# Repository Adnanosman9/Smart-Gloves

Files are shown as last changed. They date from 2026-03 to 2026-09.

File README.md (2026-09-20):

<h1 align="center">
  BdSL Translator Glove
  <br>
</h1>

<h4 align="center">
A wearable glove that translates Bangladeshi Sign Language (BdSL) into speech in real-time
</h4>

<div align="center">





</div>

## What is this?

A lot of deaf people in Bangladesh have no easy way to talk to people who don't know sign language. I wanted to fix that. Not with a camera setup that needs good lighting and a phone pointed at you the whole time, but something you actually wear and carry around. So I built it into a glove.

## How it works

There are two ways to build this depending on what you have access to.

**Option 1: Commercial flex sensors (what I recommend)**
Five 2.2" flex sensors go along each finger, held down by TPU guide segments I designed and printed. When you bend a finger, the sensor's resistance changes and the ADC picks that up. Simple and reliable.

**Option 2: Conductive TPU (only if you have your own printer)**
I originally wanted to skip commercial sensors entirely and just print the finger segments in Conductive TPU. It's piezoresistive, so resistance shifts as it bends, same idea. But no commercial print service carries conductive TPU filament, so unless you have your own printer and the filament already, this option is off the table. I learned that the hard way.

Either way, a **XIAO ESP32-C3** reads all the sensor values alongside orientation data from an **MPU-6050** IMU, maps them into a hand-geometry profile, and classifies the sign. Everything gets sent over Bluetooth LE.

No cameras. Works in the dark. Works outside. Works anywhere.

Print the finger guides here: [for flex sensors](https://github.com/Adnanosman9/Smart-Gloves/tree/main/CAD%20for%20flex%20sensor) | [for 3D-printed sensor](https://github.com/Adnanosman9/Smart-Gloves/tree/main/CAD_3d%20printed%20sensor)

---

## Addressing the Hack Club Review

The first version got flagged for two things:

> *"$80 seems a bit much for flex sensors"* and *"your CAD only shows a box, could you maybe design some flexible structure out of TPU?"*

Both fair. Here's what I changed.

**On the cost:** The original $80 estimate was for 4" flex sensors. I've since switched to 2.2" sensors at $6.86 each, which brings the total down to $68.60. BdSL uses both hands, so that's 10 fingers, 10 sensors, and $68.60 is already the cheapest I could get this to work. Not padding anything, that's just what flex sensors cost.

**On the CAD:** I redesigned the finger part properly. Each finger now has a TPU guide segment that holds the flex sensor flat against the joint. The glove actually looks like a glove now, not just a box with wires coming out of it. The wrist hub is still a box (it has to be, there's a PCB in there), but the hand part is done.

---

## The Finger Guide System

Credit to [zackfreedman](https://www.thingiverse.com/thing:1606915) for the original parametric ring glove design that I built on top of.

Find the STL [here](https://github.com/Adnanosman9/Smart-Gloves/blob/main/CAD%20for%20flex%20sensor/Ring_Glove_Parametric.stl).

Each finger gets a TPU channel segment. The sensor slides in and stays put mechanically, no glue, no tape. I made two sizes: "Long" for the index, middle, and ring fingers, and "Short" for the thumb and pinky since those are shorter and sit at a different angle.

White TPU, printable by any FDM service that does flexible filament.

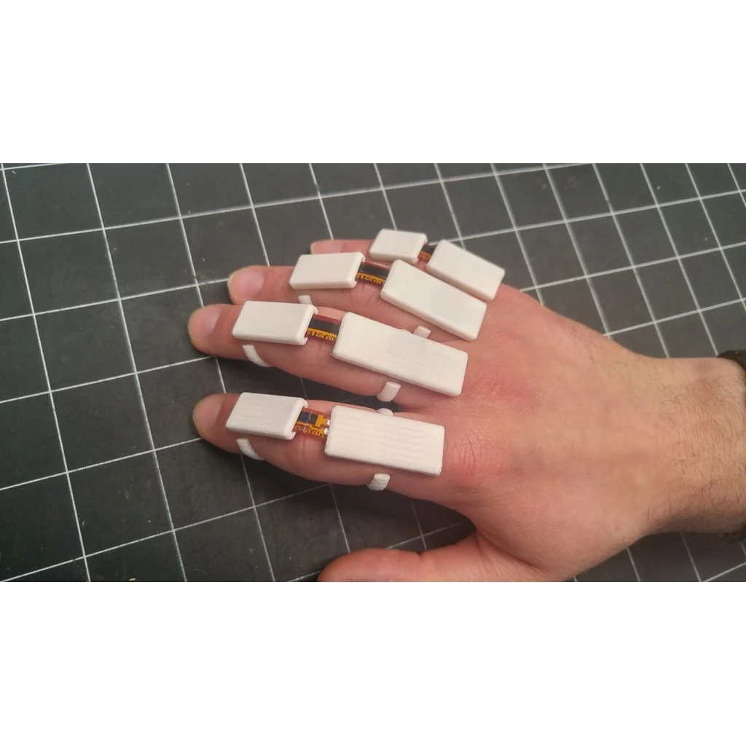
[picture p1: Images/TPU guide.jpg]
TPU finger guide segments


---

## The PCB

I designed a low-profile wrist hub in KiCad to keep everything in one place. A few things worth noting:

The **XIAO ESP32-C3** was the obvious pick: tiny footprint, built-in BLE, enough ADC pins for all five sensors. I used a **47kΩ voltage divider** on each sensor input because the flex sensors are high-impedance and need it to read reliably. Threw in **0.1µF decoupling caps** on the sensor lines too after I noticed noise in early simulations.

DRC came back 0 errors. There are some silkscreen warnings but those are just text placement things, nothing that affects the board.

**Schematic:**

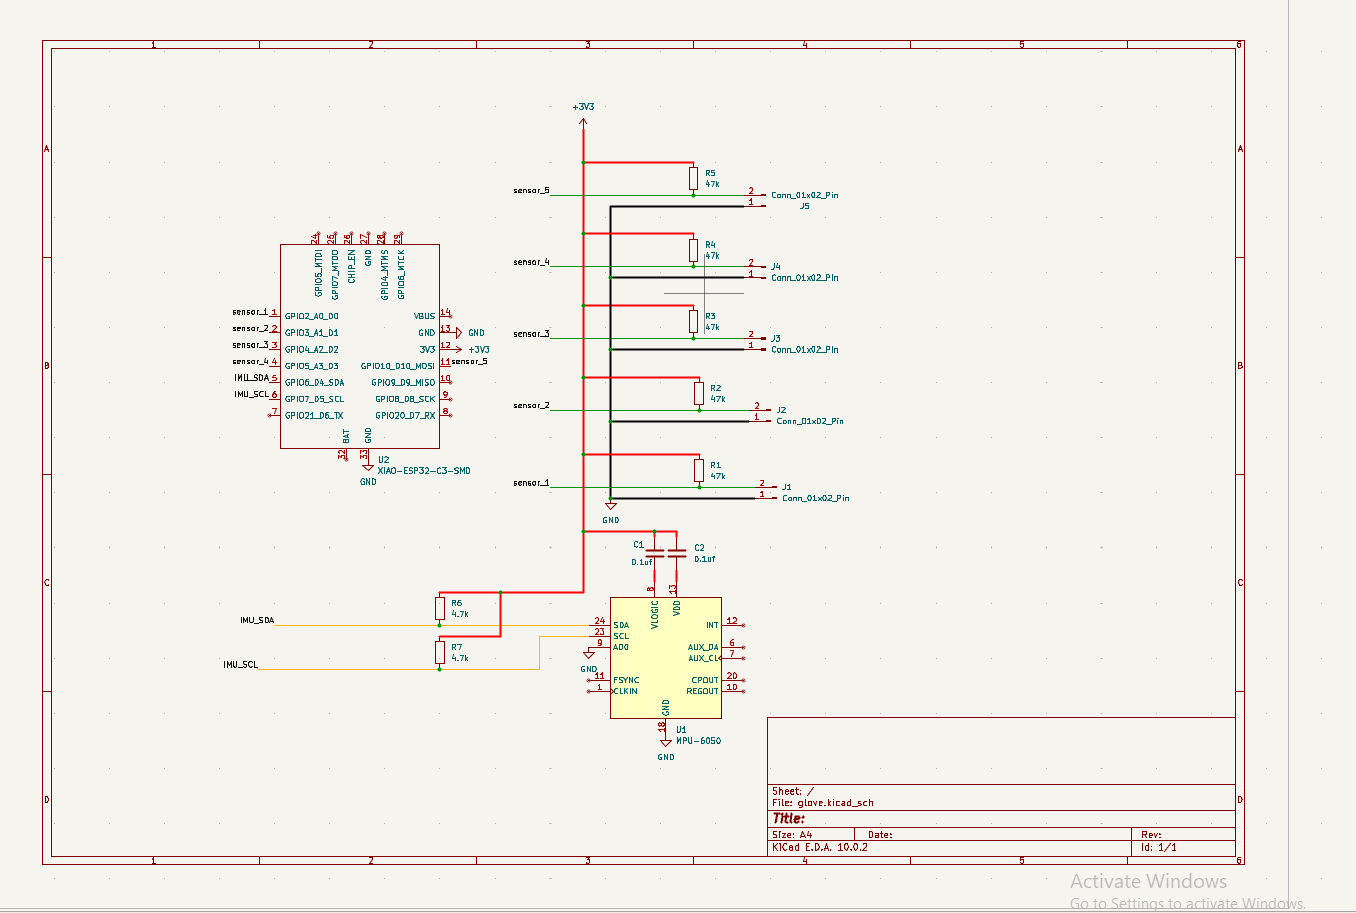
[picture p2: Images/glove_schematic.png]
Schematic


**PCB Layout:**

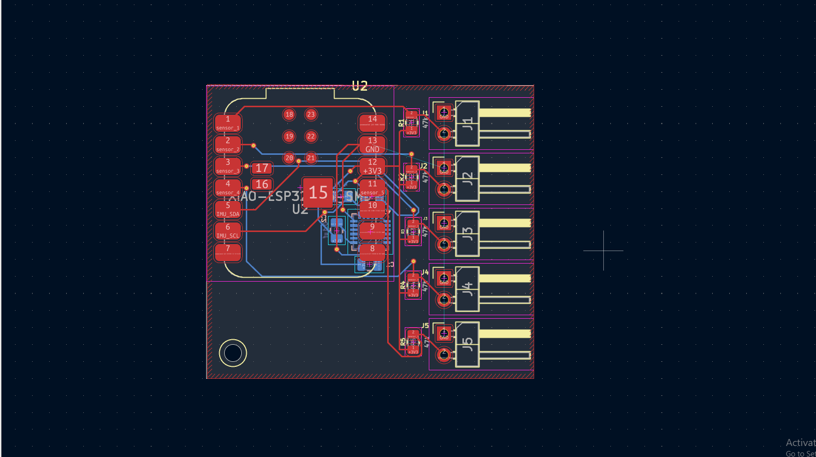
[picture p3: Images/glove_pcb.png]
PCB Layout


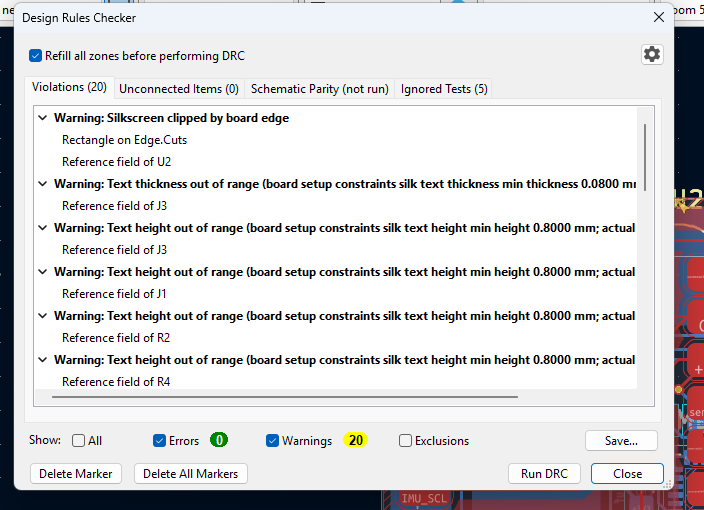
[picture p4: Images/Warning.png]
KiCad DRC: 0 errors, silkscreen warnings only


---

## The Enclosure

Designed in Fusion 360. Sits on the wrist, low-profile. The whole electronics module attaches with Velcro so you can pull it off and actually wash the glove fabric.

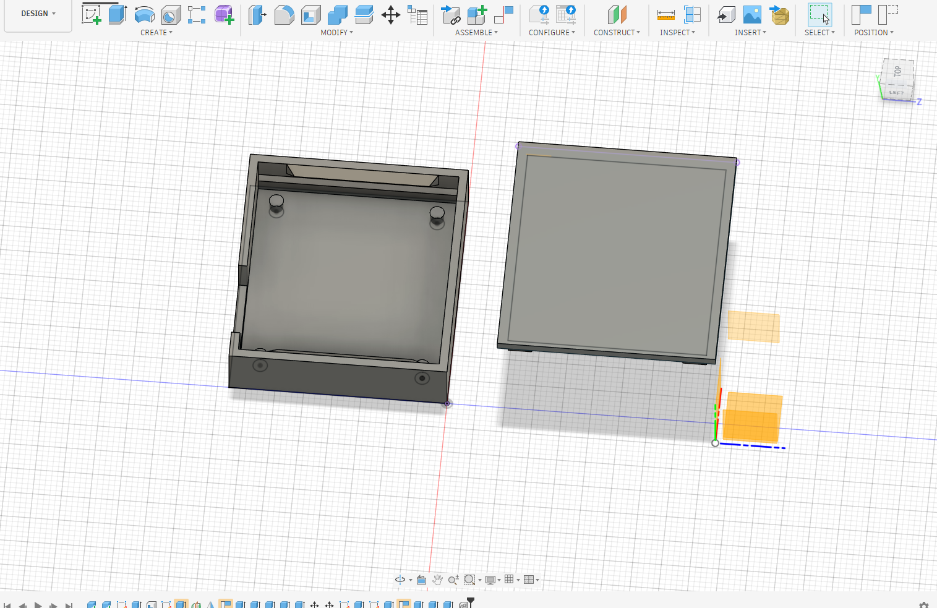
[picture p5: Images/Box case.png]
Wrist hub box


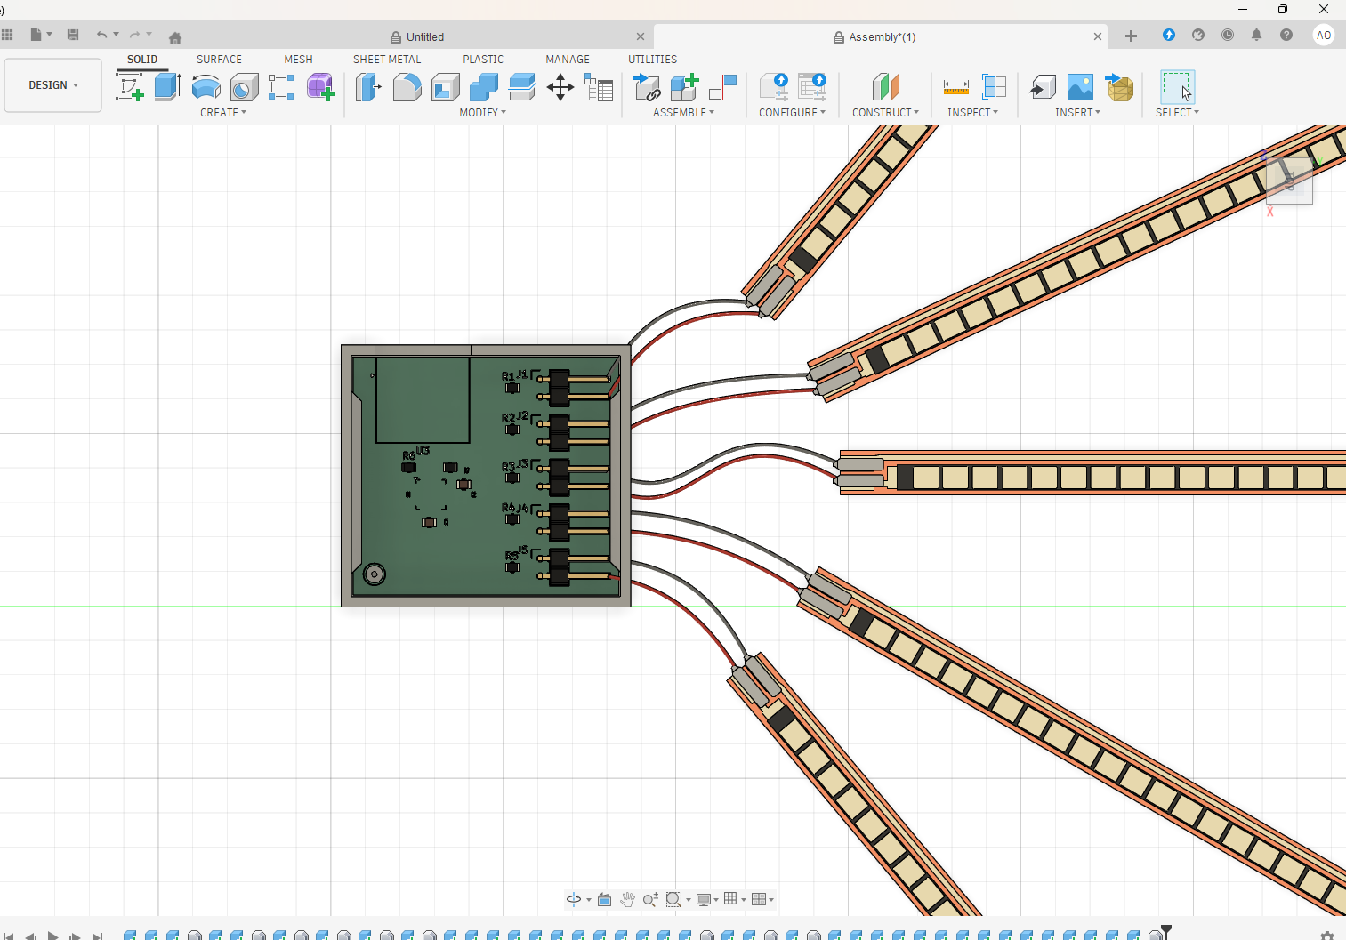
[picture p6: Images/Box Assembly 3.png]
Assembly render


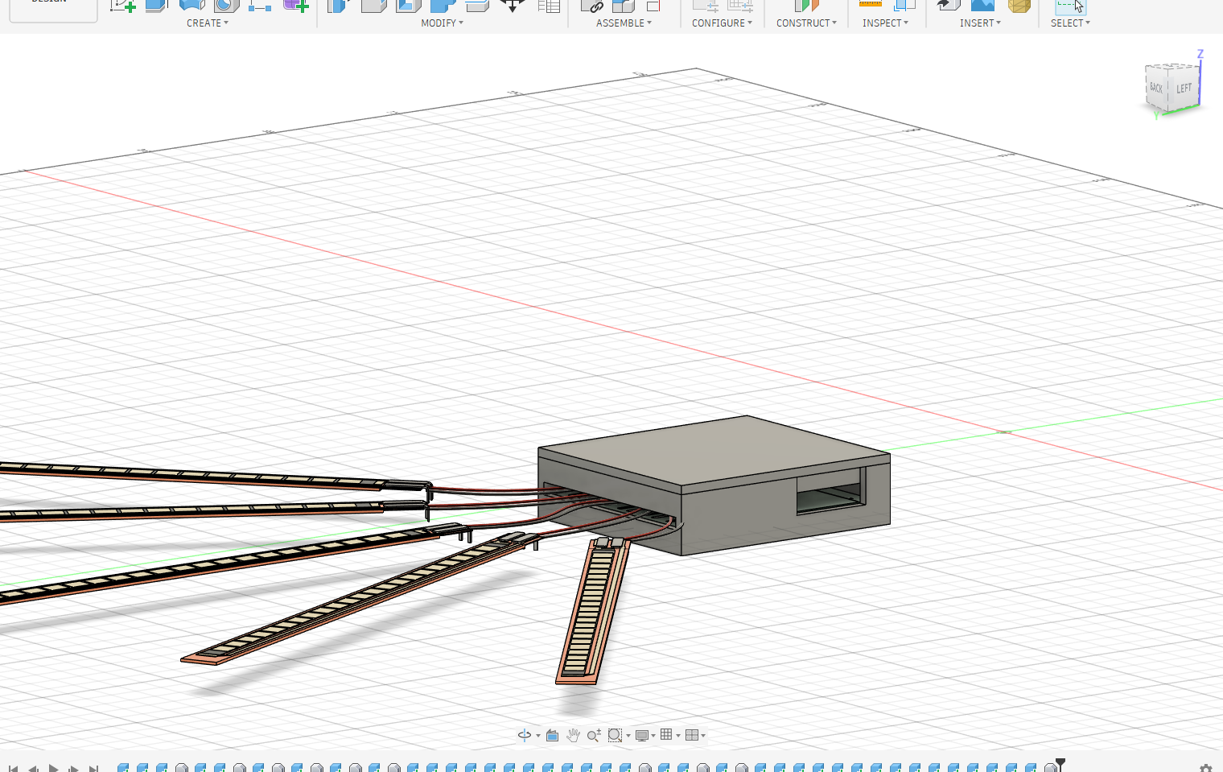
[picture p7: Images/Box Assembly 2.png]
Assembly render 2


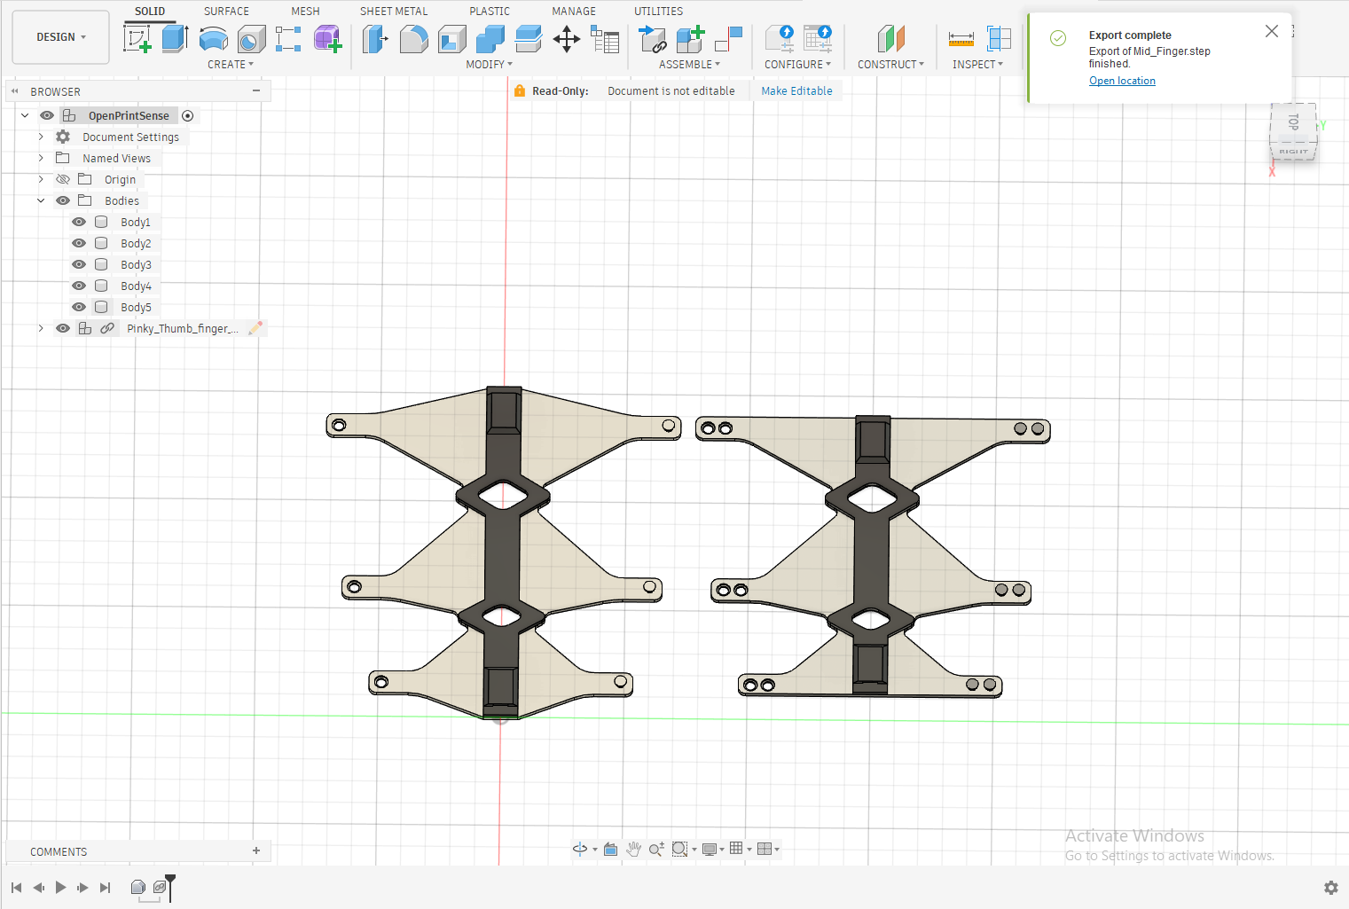
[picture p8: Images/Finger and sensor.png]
Finger segment with sensor


---

## ⚠️ Heads up on the firmware

I haven't physically tested the firmware yet. There's a real chance there are I2C pin mismatches, wrong GPIO assignments, or sensor init issues that won't show up until you actually flash and boot it. Please double-check every pin assignment against the schematic before you flash anything. First boot will probably need some debugging.

## Bill of Materials

[BOM is here](bom/BOM.csv)

## Credits

- [KiCad](https://www.kicad.org/) for PCB design
- [Autodesk Fusion 360](https://www.autodesk.com/products/fusion-360/) for the enclosure
- [Open Print Sense](https://github.com/PaBu04/OpenPrintSense/tree/main) for the 3D-printed sensor approach
- [zackfreedman](https://www.thingiverse.com/thing:1606915) for the parametric finger guide base
- [Hack Club](https://hackclub.com/) for the support

---

> GitHub [@Adnanosman](https://github.com/Adnanosman9)

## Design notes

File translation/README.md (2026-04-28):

# Translation Firmware

This is the main firmware for both gloves.  
Use this after calibration is done and your ML model is ready.

---

## Libraries

Install from Arduino Library Manager:

- ESP32 BLE Arduino (usually comes with ESP32 board package)
- Adafruit MPU6050
- Adafruit Unified Sensor
- ArduinoJson

---

## Step 1 - Calibration (Do this properly)

You need to calibrate **each glove separately**.  
Flex sensor readings are never exactly the same between hands.

Flash `calibration.ino`, open Serial Monitor, then:

1. Keep all fingers fully open (~5 seconds)
2. Then close all fingers fully (~5 seconds)
3. Copy the `openVals` and `closedVals` printed in Serial

Paste them into both:
- `glove_left.ino`
- `glove_right.ino`

```cpp
const int openVals[5]   = {your values};
const int closedVals[5] = {your values};
```

## Step 2 - Flash to Gloves

| File              | Glove | BLE Name  |
| ----------------- | ----- | --------- |
| `glove_left.ino`  | Left  | `SIGNO-L` |
| `glove_right.ino` | Right | `SIGNO-R` |

## Step 3 - Connect to App

Open the SIGNO app and press Connect.

It should automatically detect:
- SIGNO-L
- SIGNO-R

<br>

## *__I didn't have any physical component and don't have yet, so now I can't give bebug solution for every problem that will show up, I will add it up soon.__*

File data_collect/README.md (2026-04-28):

# Dataset Collection Firmware

This firmware is used to record gesture data from both gloves over USB serial.  
Each glove saves its own CSV file. Later, both files are merged and used to train the model.

---

## Requirements

- 2 gloves with ESP32-C6  
- 2 USB cables (one for each glove)  
- Arduino IDE or PlatformIO  
- Libraries:
  - Adafruit MPU6050  
  - Adafruit Unified Sensor  

---

## Before You Start (Don’t Skip This)

Open both `.ino` files and update the calibration values:

```cpp
const int openVals[5]   = {...};
const int closedVals[5] = {...};
```
Use the values from your calibration step.

If these are wrong, your flex readings will be inaccurate and you’ll likely have to redo your dataset. It’s worth checking twice here.

Recording Process
## 1. Flash both gloves

Upload:

```data_collect_left.ino``` → left glove

```data_collect_right.ino``` → right glove

## 2. Open Serial Monitors

Open two Serial Monitor windows (one for each glove)

On startup, you should see:

```label,thumb,index,middle,ring,pinky,ax,ay,az,gx,gy,gz,timestamp```

If you don’t see this, check:
- Correct COM port
- Baud rate
- Cable connection

## 3. Recording Gestures

For each gesture:
- Form the gesture and hold it steady
- Type the label (e.g. HELLO) into both Serial Monitors and press Enter
- Keep holding the gesture while it records
- Each glove records ~30 samples, then stops automatically

Repeat for all gestures.

> Try to stay still while recording — even small movements can add noise.

## 4. How Much Data?

- Minimum: ~50 samples per gesture
- Recommended: 80–100 samples

> More variation usually helps the model perform better.

## 5. Save the Data

Copy the Serial Monitor output from each window and save as:
- left_hand.csv
- right_hand.csv

## After Recording

Go to the ml/ folder and run the training script.

It will:
- Merge both CSV files using timestamps
- Train a Random Forest classifier
- Export modelWeights.js for use in the app

## CSV format reference 

| Column        | Description                            |
| ------------- | -------------------------------------- |
| label         | gesture name                           |
| thumb → pinky | flex values (0 = open, 1 = fully bent) |
| ax, ay, az    | accelerometer (g)                      |
| gx, gy, gz    | gyroscope (rad/s)                      |
| timestamp     | time in ms                             |

## Notes / Common Issues
- Both gloves need to record at the same time, otherwise merging won’t work properly
- On Windows, COM ports can change when reconnecting devices
- If Serial Monitor doesn’t connect, recheck the selected port
- If flex readings look off, redo calibration before collecting more data

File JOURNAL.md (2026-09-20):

<!--
  This journal is auto generated by Stasis.
-->

# 5/19/2026 7 PM - Changes due to sourcing issues

_Time spent: 2h_

During making the BOM, I found out that no commercial printing service prints Conductive TPU filament. 

**So it's not possible to print flex sensor out og conductive TPU unless you have own 3d printer and filament**

I re-added commercial flex sensors.

> **Flex sensors are just expensive, there's no way around it. BdSL uses both hands, so that's 10 fingers, 10 sensors. The cheapest viable 2.2" option is ~$5/sensor, which puts the total at $50. That's already the budget option. The $50 isn't extravagant; it's the floor.**





# 5/10/2026 3 PM - Commercial Sensors to Integrated 3D-Printed Hardware

_Time spent: 2h_

In the first phase of SIGNO, our real-time Sign Language translation glove relied on off-the-shelf commercial flex sensors. While functional, these sensors posed three major issues:

- **Cost: At $15–$20 per finger, the glove was too expensive for mass adoption.**

- **Durability: The rigid "box-and-wire" connection points were prone to mechanical failure.**

### **The Pivot: Sensor-less Architecture**

We’ve transitioned to a monolithic, dual-material 3D-printed exoskeleton. Instead of buying sensors, we are printing them directly into the glove's structure.

1. **Using Conductive TPU (Carbon-infused) for the sensing traces and Standard TPU for the structural base. This creates a piezoresistive effect where bending the finger changes the electrical resistance.**

2. **Shifted to the XIAO ESP32-C3. It’s incredibly small, supports Bluetooth LE for mobile app connectivity, and features a built-in battery management system for a truly wireless experience.**

3. **Developed a 4-part modular system (Long segments for long fingers, Short segments for the thumb/pinky) to ensure a universal fit and easier maintenance.**

By moving to integrated 3D-printed sensors, we have reduced the sensor BOM (Bill of Materials) cost by over 50$. This shift moves SIGNO from an "expensive prototype" to a "scalable assistive technology."








# 4/2/2026 10 AM - Revived the unfinished

_Time spent: 0.01666666666666667h_

This was a project on blueprint, but it was not finished, now i imported it to Stasis here. 











# 3/13/2026 12 PM - Finally, the firmware exists

_Time spent: 8h_

## The Brain and Neurons

Okay so the hardware has been sitting there looking pretty for a while now. Today I actually wrote the firmware. All of it.

Added a proper directories for each;
- [Data Collect](https://github.com/Adnanosman9/Smart-Gloves/tree/main/data_collect) - for recording labeled gesture CSVs from both gloves
- [Translation](https://github.com/Adnanosman9/Smart-Gloves/tree/main/translation) - the main BLE firmware that streams sensor data to the app
- [App](https://github.com/Adnanosman9/Smart-Gloves/tree/main/app) - the React Native app that connects, classifies and plays sign gesture loud

Also there is a caution that the firmware isn't physically tested yet because honestly it probably has at least one I2C pin mismatch and I'd rather admit that upfront than pretend everything works.

The SDA/SCL pins in the README said GPIO 6/7 but the schematic says IO8/IO9. Classic. Fixed that too.

At least the glove looks good while the firmware is mid.








# 2/13/2026 12 PM - 404

_Time spent: 1h_

There is a special kind of problem in writing `i2c_read_bytes()` while I have nothing connected to the pins. I'm currently simulating the project gestures with random number of values of flex sensor and IMU.

HOnestly, This things is a total frustration when I can't check what I am writing.





# 2/12/2026 9 PM - Repository Updated

_Time spent: 1h_

After finalizing the hardware designs, spent some time to arrange every step file and PCB gerber file in a folder. Also added several images showing the path. This project has a snap fit box and a PCB holding Microcontrollers and IMU. To make it understandable I tried to make the read me perfect. I guess it will be a good overview to determine why and how the project is made. 

Repo : [GitHub](https://github.com/Adnanosman9/Smart-Gloves)

Github



# 2/12/2026 3 PM - PCB warnings

_Time spent: 1h_

I was just about to export my Gerber files when KiCad decided to humble me with 2 Warnings.
I thought I made any kind of mistake but at the end as usual I found out that I accidently deleted my copper GND layer.

After adding the copper layer, here was 2 warnings and thoose were just for a silkscreen boundery and I think it doesn't create mess. 

_glove — PCB Editor 2_12_2026 3_03_32 PM



# 2/10/2026 11 PM - Made a snap fit box case.

_Time spent: 1h_

To place the pcb on the glove properly, I made a box to place the PCB properly. I used fusion 360 to make that. I made enough holes in the case to connect the external wires and flex sensors.

Box;
Box case

Box with wiring
Box Assembly 2




# 2/10/2026 8 PM - I created a PCB

_Time spent: 1.5h_

Flex sensor is a variable resistor that needs voltage devider to give values. To connect every flex sensor with the microcontroller it will need many cabkle and as we are planning to install it on hands then too much wires might look messy. To avoid these messy problems we are creating a PCB with esp32 c6, MPU6050 on board and 5 2pin connectors to connect Fles sensors externally. 

Glove_PCB

Glove_Schemetic




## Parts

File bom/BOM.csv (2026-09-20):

Name | Purpose | Qty | Total (USD) | Link | Distributor | Note
Flex sensor | Main part to calculate physical bending | 10 | 68.6 | https://www.daraz.com.bd/products/limited-time-offer-flex-sensor-22-inch-bend-flex-sensor-for-robotic-hand-electronic-gloves-flex22-flex45-flex-sensor-45-i157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 | daraz
TPU guide | TPU guide rail to hold the flex sensor | 10 | $6.22 | https://jlc3dp.com/?spm=Jlc3dp.Homepage.1001 | JLC3dp
PCB | Main communication source | 1 | $2.00 | https://jlcpcb.com/ | JLCPCB
Resistor | 47kΩ | 10 | $1.00 | https://www.daraz.com.bd/products/resistor-300pcs-mix-10-220-270-330-470-560-1k-12k-22k-33k-47k-10k-47k-100k-220k-470k-ohm-14w-5-carbon-film-resistor-300pcs-m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 | daraz
Resistor | 4.7kΩ | 4 | $0.20 | https://www.daraz.com.bd/products/47k-ohm-14w-530-i161032855-s1092924449.html?c=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 | daraz
Capacitor | 0.1uF | 4 | $3.00 | https://www.daraz.com.bd/products/100pcslot-0603-smd-chip-multilayer-ceramic-capacitor-05pf22uf-10pf-100pf-1nf-10nf-100nf-01uf-1uf-22uf-mlcc-chip-capacitor-i5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 | daraz
Male Header Pins | 1x02 Pin | 10 | $1.00 | https://www.daraz.com.bd/products/2-40x1-40x1-90-254mm-i145650295-s1071048718.html?c=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 | daraz
XIAO ESP32-C3 | Wi-Fi/BLE MCU | 2 | $24.00 | https://www.daraz.com.bd/products/seeed-xiao-esp32-c3c6s3-mini-board-wifi-6ble-53-for-smart-homeindustryarduino-iot-edge-ai-projects-i556148401-s2587969163.html | daraz
MPU-6050 | 6-DoF IMU | 2 | $6.00 | https://www.daraz.com.bd/products/gy521-gy-521-mpu-6050-mpu6050-mpu-6050-dc-3v-5v-3-tr-iple-3-ax-is-an-alog-gyr-arduino-iic-i2c-gy-ro-i147752019-s1073498031.h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 | daraz
3d printed flex sensor + Fingers (Not applicable in our project, we are already using commercial sensors) | 3D printed parts for flex sensor and fingers | 10 | $30.00 | https://www.pcbway.com/ | PCBWay | (If using commercial flex sensor then you can skip this part. This is for custom flex sensor and fingers. You can also use 3D printing service from any local 3D printing service provider. We are not usning this due to we don't have access to conductive TPU filament)
 |  |  | Total = $111.82

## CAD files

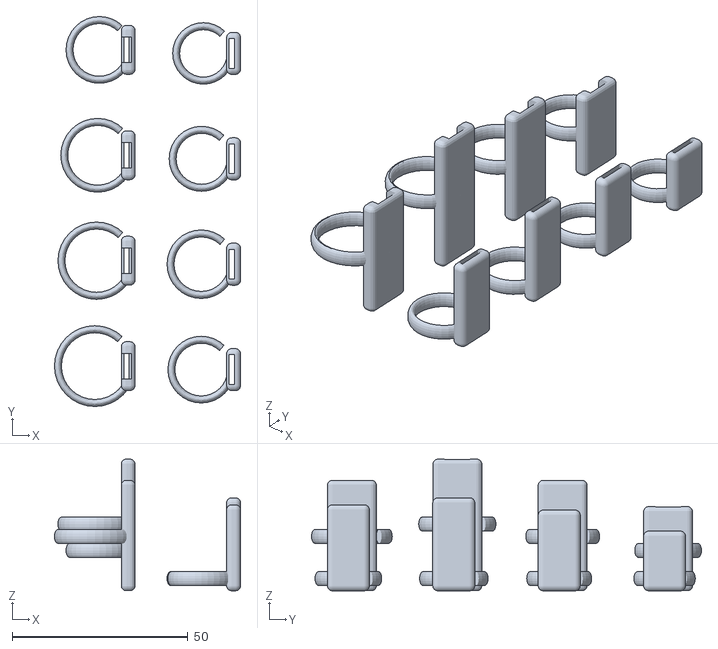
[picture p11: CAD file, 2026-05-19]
CAD for flex sensor/Ring_Glove_Parametric.stl
53.0 x 111.0 x 37.5

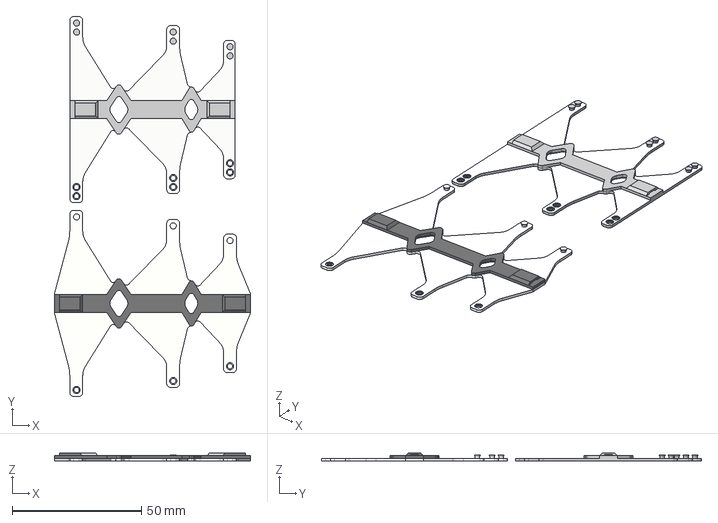
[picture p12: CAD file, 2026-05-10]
CAD_3d printed sensor/3d_printed sensor.step
76.0 x 147.0 x 3.00 mm

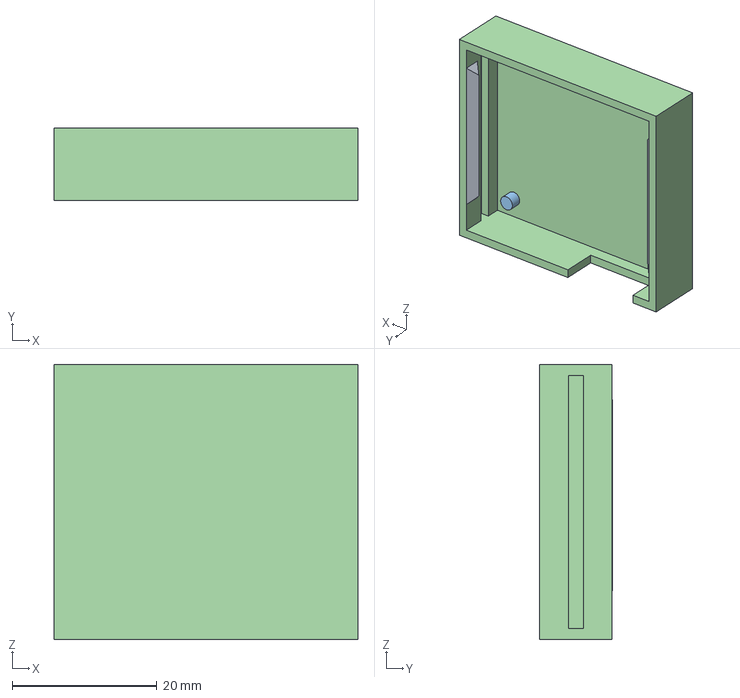
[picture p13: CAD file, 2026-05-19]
CAD for flex sensor/Bottom case.step
42.0 x 10.0 x 38.0 mm

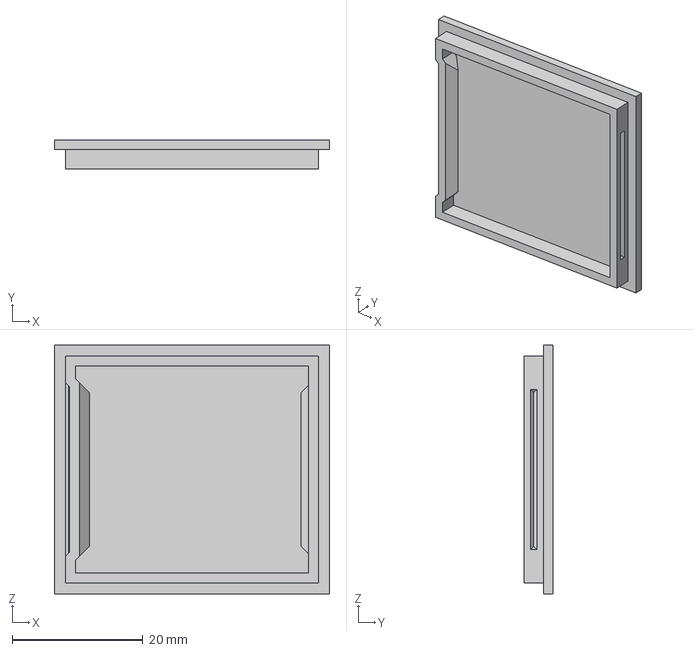
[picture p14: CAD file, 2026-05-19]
CAD for flex sensor/Top case.step
42.0 x 4.50 x 38.0 mm

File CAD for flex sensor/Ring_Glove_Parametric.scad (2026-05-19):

/**************************************************************************************\
| Parametric Data Glove Finger Sensors
| Project codename "Grip"
| Designed by Zack Freedman of Voidstar Lab
| 
| Print as rendered with three outer layers using supports for maximum strength.
| PLA and ABS are both suitably durable.
|
| Insert a polyimide (Kapton) laminated Flexpoint flex sensor, with socket, 
| into each first segment.
|
| Don first segments, then don second segments. 
| Thread exposed sensor through second segment.
|
| Read using a voltage divider and ADC.
| Flex sensors are high impedance. Minimize lead length.
|
| Thumb was intentionally omitted. This configuration cannot measure thumb flexure
| without compromising manual dexterity.
|
| Overly snug rings and sharp edges can cut off blood flow and pinch nerves.
| Loose wires can snag on objects.
| Prioritize your biology and augment safely.
|
| Licensed Creative Commons 3.5 Attribution Noncommercial.
| Do not use for safety-critical applications.
\**************************************************************************************/

/* [Settings] */

// Which finger would you like to print?
part = "all"; // [all:All fingers,index:Index only,middle:Middle only,ring:Ring finger only,pinky:Pinky only,thumb:No Thumb]

/* [Index] */

// Millimeters from knuckle to knuckle. This segment is closest to your palm.
index_finger_first_segment_length = 30.5; // [15:0.5:50]

// Millimeters from knuckle to knuckle. This segment is between the fingertip and the first segment.
index_finger_second_segment_length = 23.5; // [15:0.5:50]

// Adjust for a snug fit. Use trial and error. Units of mm.
index_finger_first_segment_ring_diameter = 21; // [10:0.5:35]

// Adjust for a snug fit. Use trial and error. Units of mm.
index_finger_second_segment_ring_diameter = 17; // [10:0.5:35]

// Adjust to center the segment between your knuckles. Units of mm. 
index_finger_first_segment_ring_placement = 14; // [0:0.5:50]

// Adjust to center the segment between your knuckles. Units of mm. 
index_finger_second_segment_ring_placement = 2 ; // [0:0.5:50]

// Adjust to minimize the amount of exposed sensor
index_finger_sensor_inset = 13; // [0:0.5:35]

// Tune if ring is off-center or uncomfortable.
index_finger_first_segment_ring_offset = 3.5; // [0:0.1:5]

// Tune if ring is off-center or uncomfortable.
index_finger_second_segment_ring_offset = 3.2; // [0:0.1:5]


/* [Middle] */

// Millimeters from knuckle to knuckle. This segment is closest to your palm.
middle_finger_first_segment_length = 36.5; // [15:0.5:50]

// Millimeters from knuckle to knuckle. This segment is between the fingertip and the first segment.
middle_finger_second_segment_length = 25.5; // [15:0.5:50]

// Adjust for a snug fit. Use trial and error. Units of mm.
middle_finger_first_segment_ring_diameter = 20; // [10:0.5:35]

// Adjust for a snug fit. Use trial and error. Units of mm.
middle_finger_second_segment_ring_diameter = 17.5; // [10:0.5:35]

// Adjust to center the segment between your knuckles. Units of mm. 
middle_finger_first_segment_ring_placement = 17.5; // [0:0.5:50]

// Adjust to center the segment between your knuckles. Units of mm. 
middle_finger_second_segment_ring_placement = 2 ; // [0:0.5:50]

// Adjust to minimize the amount of exposed sensor
middle_finger_sensor_inset = 13; // [0:0.5:35]

// Tune if ring is off-center or uncomfortable.
middle_finger_first_segment_ring_offset = 3; // [0:0.1:5]

// Tune if ring is off-center or uncomfortable.
middle_finger_second_segment_ring_offset = 3.2; // [0:0.1:5]


/* [Ringfinger] */

// Millimeters from knuckle to knuckle. This segment is closest to your palm.
ring_finger_first_segment_length = 30.5; // [15:0.5:50]

// Millimeters from knuckle to knuckle. This segment is between the fingertip and the first segment.
ring_finger_second_segment_length = 22; // [15:0.5:50]

// Adjust for a snug fit. Use trial and error. Units of mm.
ring_finger_first_segment_ring_diameter = 19; // [10:0.5:35]

// Adjust for a snug fit. Use trial and error. Units of mm.
ring_finger_second_segment_ring_diameter = 16.5; // [10:0.5:35]

// Adjust to center the segment between your knuckles. Units of mm. 
ring_finger_first_segment_ring_placement = 14; // [0:0.5:50]

// Adjust to center the segment between your knuckles. Units of mm. 
ring_finger_second_segment_ring_placement = 2 ; // [0:0.5:50]

// Adjust to minimize the amount of exposed sensor
ring_finger_sensor_inset = 13; // [0:0.5:35]

// Tune if ring is off-center or uncomfortable.
ring_finger_first_segment_ring_offset = 2.7; // [0:0.1:5]

// Tune if ring is off-center or uncomfortable.
ring_finger_second_segment_ring_offset = 3.1; // [0:0.1:5]

/* [Pinky] */

// Millimeters from knuckle to knuckle. This segment is closest to your palm.
pinky_finger_first_segment_length = 23; // [15:0.5:50]

// Millimeters from knuckle to knuckle. This segment is between the fingertip and the first segment.
pinky_finger_second_segment_length = 16; // [15:0.5:50]

// Adjust for a snug fit. Use trial and error. Units of mm.
pinky_finger_first_segment_ring_diameter = 17; // [10:0.5:35]

// Adjust for a snug fit. Use trial and error. Units of mm.
pinky_finger_second_segment_ring_diameter = 15.5; // [10:0.5:35]

// Adjust to center the segment between your knuckles. Units of mm. 
pinky_finger_first_segment_ring_placement = 10; // [0:0.5:50]

// Adjust to center the segment between your knuckles. Units of mm. 
pinky_finger_second_segment_ring_placement = 2 ; // [0:0.5:50]

// Adjust to minimize the amount of exposed sensor
pinky_finger_sensor_inset = 0; // [0:0.5:35]

// Tune if ring is off-center or uncomfortable.
pinky_finger_first_segment_ring_offset = 2.2; // [0:0.1:5]

// Tune if ring is off-center or uncomfortable.
pinky_finger_second_segment_ring_offset = 2.6; // [0:0.1:5]

/* [Hidden] */

outerAWidth = 14;
outerBWidth = 12;

socketMaxWidth = 11;
flexCutoutWidth = 8.5;

module socket(socketSetback) {
    innerHeight = 4;
    innerOffset = -1;

    difference() {
        translate([innerOffset, 0, socketSetback]) cube([innerHeight, socketMaxWidth, 9.4 + 1.25]);
        
        translate([innerOffset, 0, socketSetback]) cube([innerHeight, 1.25, 1.55]);
        
        translate([innerOffset, socketMaxWidth - 1.25, socketSetback]) cube([innerHeight, 1.25, 1.55]);
    }
    
    translate([innerOffset, (socketMaxWidth - 7.3) / 2, socketSetback]) cube([innerHeight, 7.3, 50]);
            
    translate([0.75, (socketMaxWidth - flexCutoutWidth) / 2, socketSetback - 49]) flexSensorCutout();
}

module flexSensorCutout() {
    cube([1.5, flexCutoutWidth, 50], false);
}

module ring(diameter, reliefAngle=0) {
    scale([1, 1, 2]) {
            difference() {
            // Ring
            rotate_extrude($fn=32) translate([diameter / 2, 0, 0]) circle(r=1, $fn=16);
            
            // Relief
            // TODO: rotate_extrude() instead once I update SCAD
            rotate([0, 0, reliefAngle]) translate([diameter / 2 - 1, -3, 0]) cube([5, 5, 3], true);
        }
    }
}

module fingerA(length, ringDiameter, ringPlacement, ringOffset, sensorInset) {
    difference() {
        union() {            
            chamfer = 1.5;
            intersection() {
                translate([chamfer, chamfer,0]) minkowski() {
                    $fn=16;
                    cube([4 - chamfer * 2, outerAWidth - chamfer * 2, length - 2], false);
                    sphere(r=chamfer);
                }
                
            }   
            
            translate([-(4 + ringOffset), outerAWidth / 2, ringPlacement]) ring(ringDiameter, 50);
        }

        translate([0, (outerAWidth - socketMaxWidth) / 2, -.5])
            socket(sensorInset);
    }
}

module fingerB(length, ringDiameter, ringPlacement, ringOffset) {
    difference() {
        union() {
            chamfer = 1.5;
            translate([chamfer, chamfer, 0]) minkowski() {
                $fn=32;
                cube([4 - chamfer * 2, outerBWidth - chamfer * 2, length - 2], false);
                sphere(r=chamfer);
            }
            
            translate([-(4 + ringOffset), outerBWidth / 2, ringPlacement]) ring(ringDiameter, 50);
        }
        
        translate([.75, (outerBWidth - flexCutoutWidth) / 2, -5]) flexSensorCutout();
    }
}

module indexFinger() {
    fingerA(
        index_finger_first_segment_length, 
        index_finger_first_segment_ring_diameter,
        index_finger_first_segment_ring_placement, 
        index_finger_first_segment_ring_offset, 
        index_finger_sensor_inset);
    
    translate([30, 0, 0]) fingerB(
        index_finger_second_segment_length, 
        index_finger_second_segment_ring_diameter,
        index_finger_second_segment_ring_placement,
        index_finger_second_segment_ring_offset);
}
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

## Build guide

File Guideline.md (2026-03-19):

# Building This Project - A Guide

This is for anyone trying to build the gloves from scratch or contribute to the project. I'll walk through the full process in the order you actually need to do things.

---

## What this is

Two gloves, each running an ESP32-C6 with 5 flex sensors and an MPU6050. They send sensor data over BLE to a React Native app, which classifies the gesture and reads it out loud. No internet, no camera, runs fully on-device.

---

## What you need installed
 
- [Arduino IDE](https://www.arduino.cc/en/software) - with the ESP32 board package installed (add `https://raw.githubusercontent.com/espressif/arduino-esp32/gh-pages/package_esp32_index.json` to board manager URLs)
- [Node.js](https://nodejs.org/en/download) - LTS version is fine, needed for the React Native app
- [React Native CLI](https://reactnative.dev/docs/environment-setup) -follow the "React Native CLI Quickstart" tab, not Expo
- [Python 3](https://www.python.org/downloads/) -for the ML training pipeline when that's ready
- An Android or iOS phone for the app
- Download the **[Signo APP](app/app-release.apk)** from here

---

## Step 0 - Hardware first

Order from the BOM before doing anything else. Flex sensors are the expensive part - 10 of them will run you around 20k BDT — and if you're buying locally they can take a while to arrive.

PCB files are in `/PCB/`. Take `Gerber.zip` and upload it to JLCPCB or wherever you get PCBs made. 2-layer, standard settings, nothing special.

Enclosure files are in `/CAD/`. `.f3d` opens in Fusion 360, `.step` works in pretty much everything else. Print both halves and check the fit before you start mounting anything.

---

## Step 1 - Calibrate before anything else

The flex sensors read differently depending on how they sit on your hand and how tight the glove is. The placeholder values in the firmware (`openVals = 400`, `closedVals = 900`) are just guesses - you need real numbers from your actual gloves.

Flash `translation/calibration.ino` to an ESP32, open Serial Monitor at `115200 baud`, and follow what it prints. It'll ask you to hold fingers open, then close them, and spit out your values:

```cpp
const int openVals[5]   = {412, 398, 405, 410, 395};
const int closedVals[5] = {887, 901, 876, 892, 910};
```

Do this for both gloves separately. Left and right hands flex differently so the numbers won't match.

---

## Step 2 - Record gesture data

Paste your calibration values into `data_collect/data_collect_left.ino` and `data_collect/data_collect_right.ino` - the arrays are near the top, hard to miss.

Flash left to left, right to right. Open two separate Arduino IDE windows with Serial Monitor at `115200 baud` each.

To record a gesture — form it with both hands, type the label in both Serial Monitors at roughly the same time and hit Enter, hold the gesture still for about 1.5 seconds. It records 30 samples then stops. Repeat for the next one.

Copy the output from each window into `left_hand.csv` and `right_hand.csv`.

50 samples per gesture is the minimum to get anything reasonable out of the model. 100 is better. If a gesture looks noisy, record more.

One thing to watch: both ESPs timestamp using their own uptime clock from whenever they booted, not actual wall time. If you started them at different times the timestamps won't line up directly - the merge script will need to handle that offset.

---

## Step 3 - Train the model

The training scripts aren't in the repo yet. This part is still being worked on.

When it's ready, it'll merge both CSVs, train a Random Forest, and export `modelWeights.js` into `app/src/ml/`. The app imports that file on startup - if it's missing, the app crashes immediately.

---

## Step 4 - Flash the translation firmware

Same deal as data collection - paste your calibration values into `translation/glove_left.ino` and `translation/glove_right.ino` before flashing.

Left glove advertises as `SIGNO-L`, right as `SIGNO-R`. The app looks for exactly those names when scanning.

---

## Step 5 - Run the app

```bash
cd app
npm install
npx react-native run-android
# or
npx react-native run-ios
```

On Android you'll need to grant `BLUETOOTH_SCAN`, `BLUETOOTH_CONNECT`, and `ACCESS_FINE_LOCATION` - the permissions are already in the manifest, just make sure they're accepted on the device. Tap Connect and it'll find both gloves on its own.

---

## Things that might bite you

The firmware hasn't been tested on real hardware yet so there will probably be some debugging involved. A few things to check before you get frustrated;

**modelWeights.js** - the app will crash without it. Don't try to run the app until the model is trained and the file is in place.

**BLE not advertising on first boot** - occasionally the BLE stack on ESP32 doesn't start clean after a fresh flash. Power cycle the board if the app can't find a glove.

---

## Contributing

If you fix any of the above or build out the ML training pipeline, PRs are welcome. One thing per PR makes it easier to review.

---

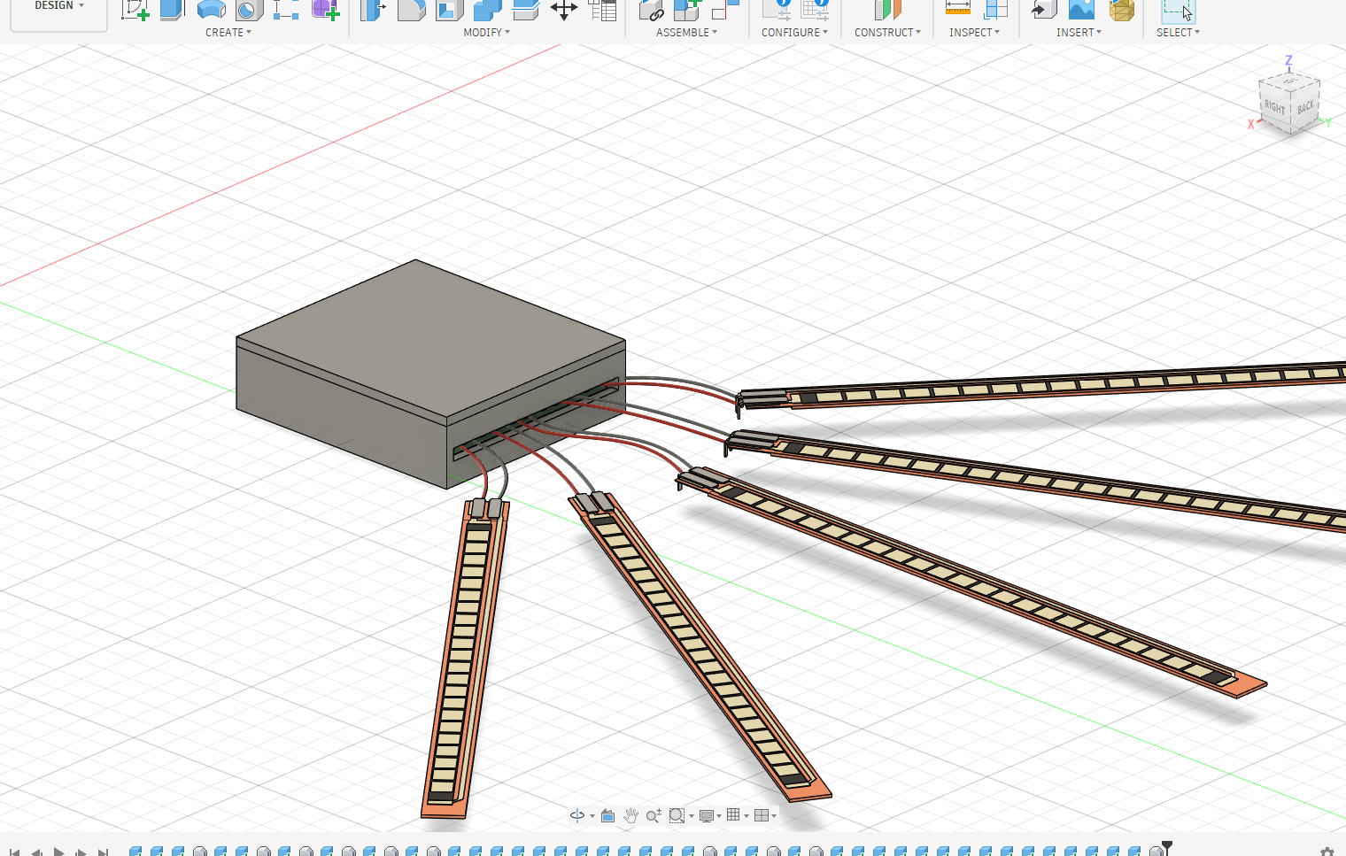
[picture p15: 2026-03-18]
Images/Box Assembly 1.png

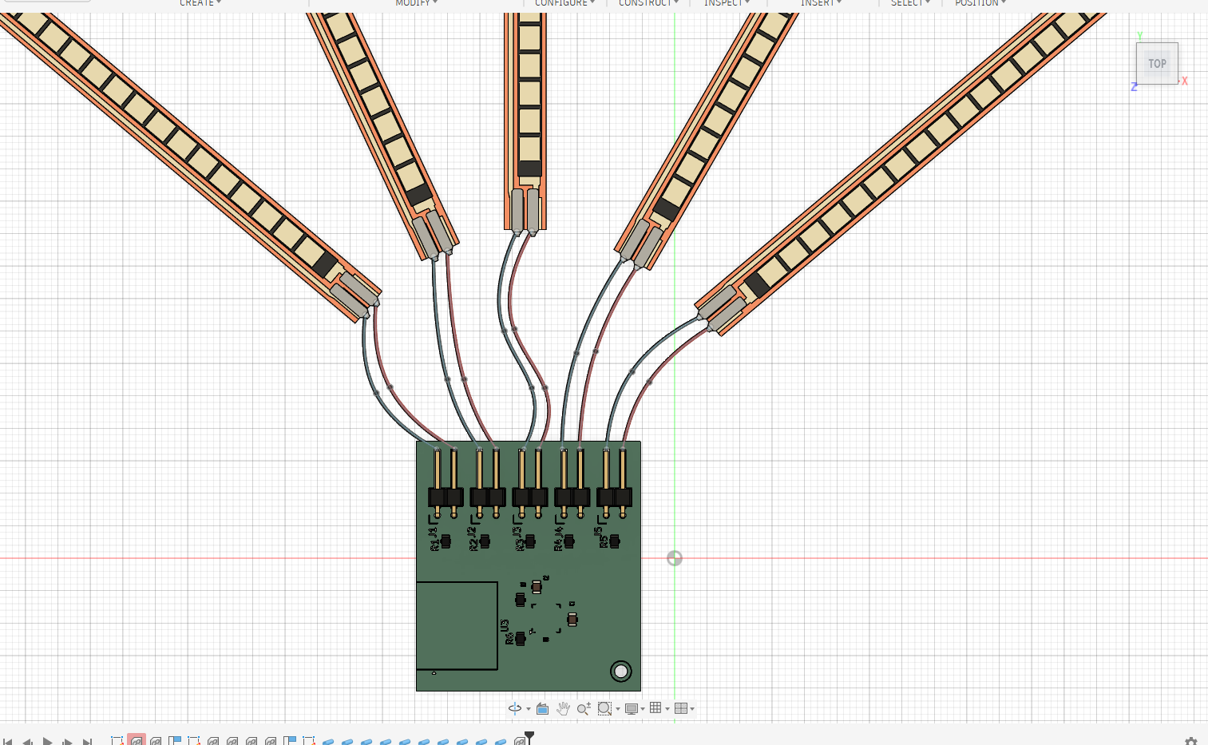
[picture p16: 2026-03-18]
Images/Wiring Diagram.png

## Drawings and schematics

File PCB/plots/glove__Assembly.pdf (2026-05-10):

# J3 J1 R2 R4 R1 U2

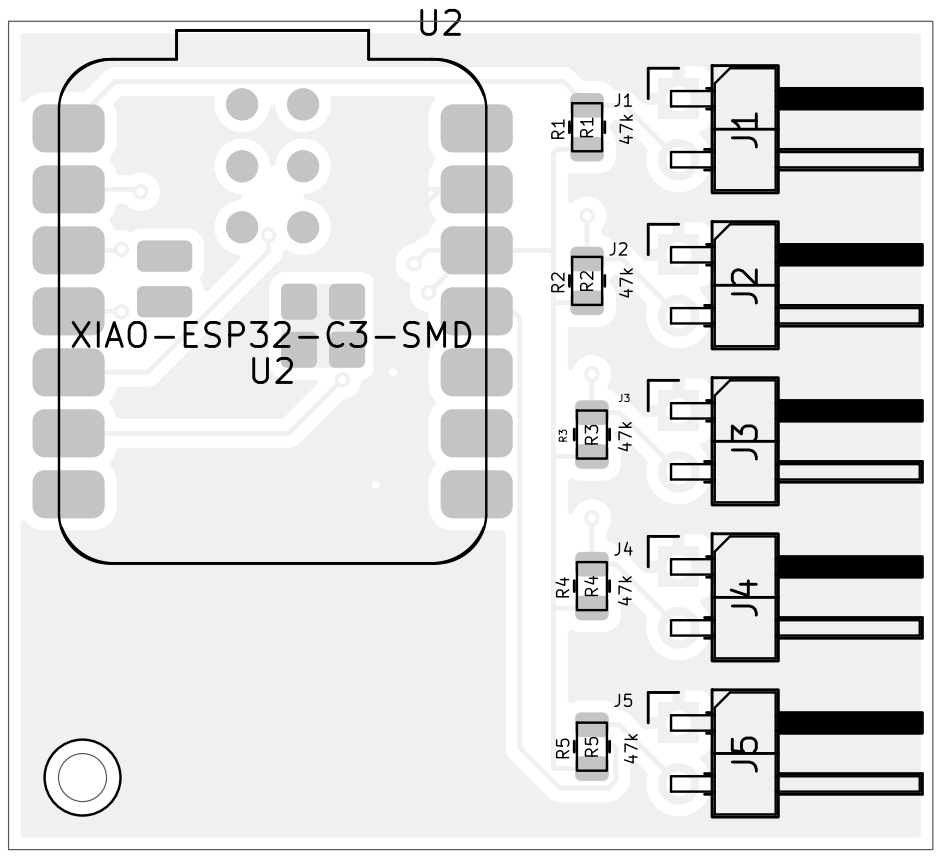
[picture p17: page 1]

Sheet: Black And White TOP
File: glove.kicad_pcb
Title:
KiCad E.D.A. 10.0.2

## 4.7k R7 0.1uf C2

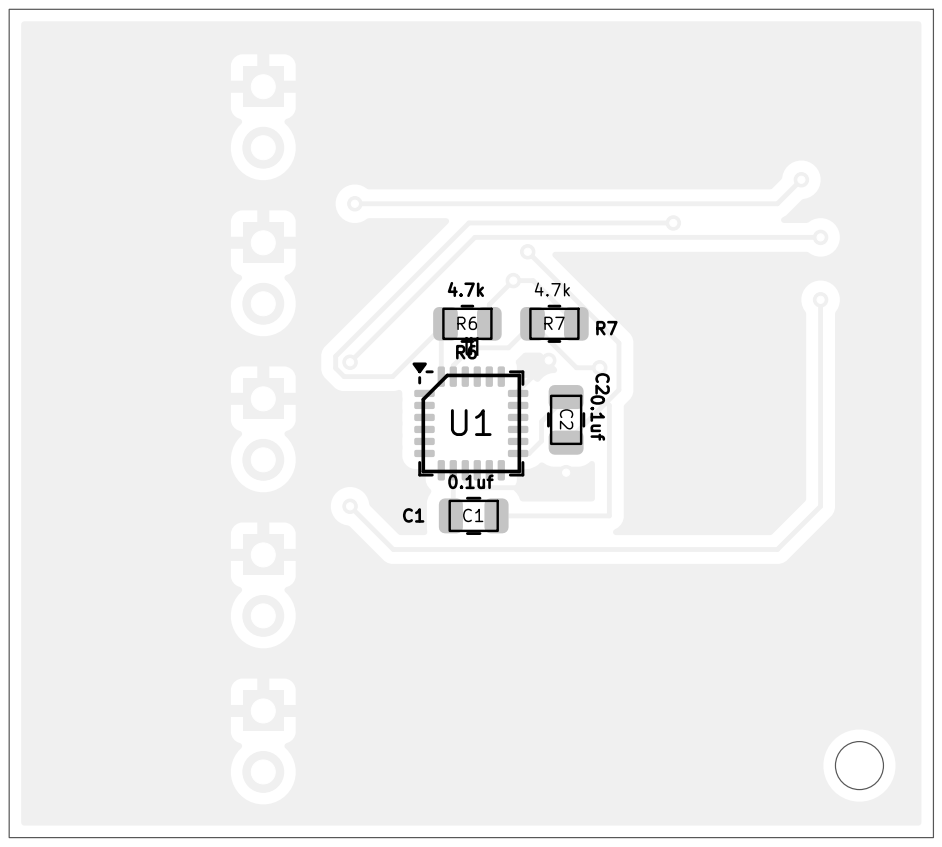
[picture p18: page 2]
D Date:; Size: A4; Rev:

Board2Pdf: Black And White BOT - Page 2/2

Sheet: Black And White BOT
File: glove.kicad_pcb
Title:
KiCad E.D.A. 10.0.2

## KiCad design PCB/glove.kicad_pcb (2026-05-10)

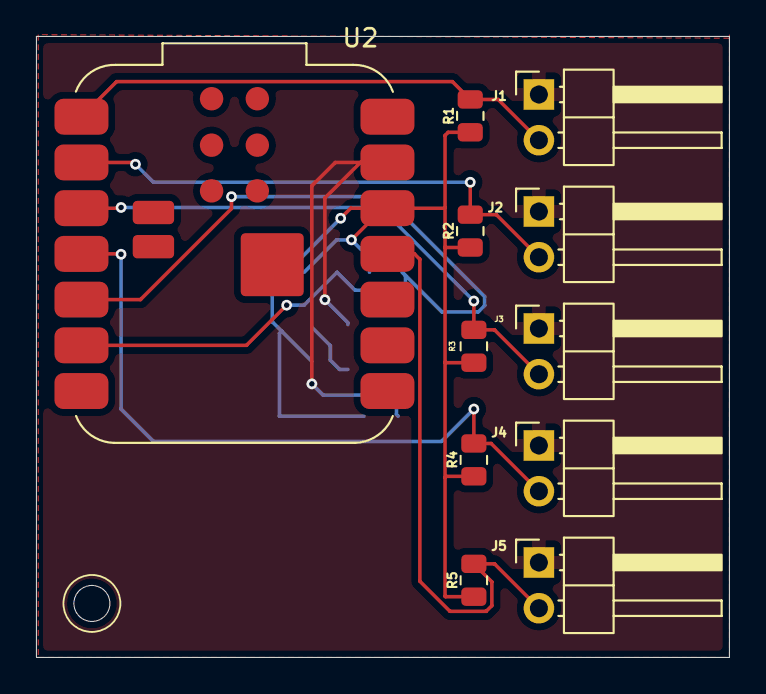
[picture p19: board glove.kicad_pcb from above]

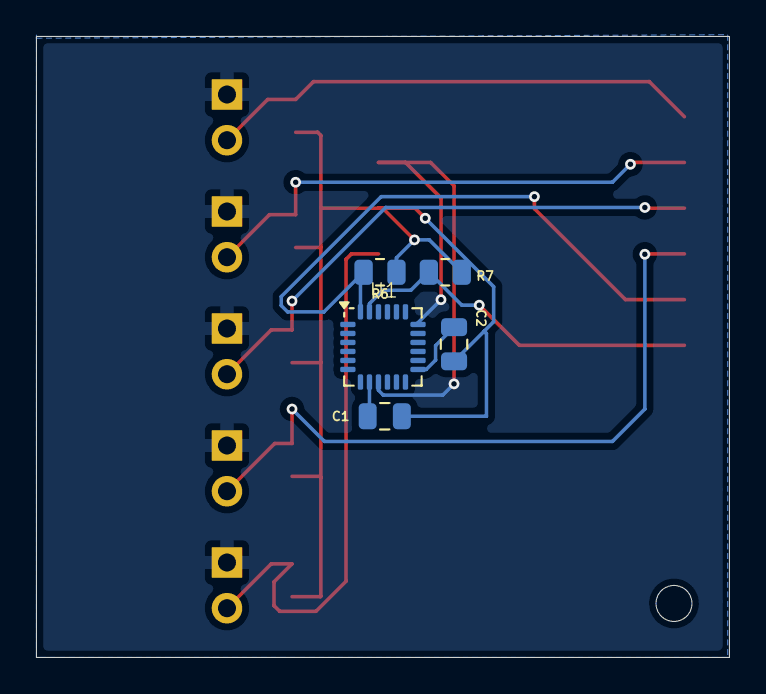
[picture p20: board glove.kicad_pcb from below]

Board: 2 copper layers, 38.5 x 34.5 mm, 16 parts (5 on the bottom side), 11 nets.

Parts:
C1, C2: 0.1uf; C_0805_2012Metric
J1, J2, J3, J4, J5: Conn_01x02_Pin; PinHeader_1x02_P2.54mm_Horizontal
R1, R2, R3, R4, R5: 47k; R_0805_2012Metric
R6, R7: 4.7k; R_0805_2012Metric
U1: MPU-6050; InvenSense_QFN-24_4x4mm_P0.5mm
U2: XIAO-ESP32-C3-SMD; MCU_Seeed_ESP32C3

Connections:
+3V3: C1.1, C2.1, R1.1, R2.1, R3.1, R4.1, R5.1, R6.1, R7.1, U2.12 (3V3)
/IMU_SCL: R7.2, U1.23 (SCL), U2.6 (GPIO7_D5_SCL)
/IMU_SDA: R6.2, U1.24 (SDA), U2.5 (GPIO6_D4_SDA)
/sensor_1: J1.2, R1.2, U2.1 (GPIO2_A0_D0)
/sensor_2: J2.2, R2.2, U2.2 (GPIO3_A1_D1)
/sensor_3: J3.2, R3.2, U2.3 (GPIO4_A2_D2)
/sensor_4: J4.2, R4.2, U2.4 (GPIO5_A3_D3)
/sensor_5: J5.2, R5.2, U2.11 (GPIO10_D10_MOSI)
GND: J1.1, J2.1, J3.1, J4.1, J5.1, U1.9 (AD0), U1.18 (GND), U2.13 (GND)
unnamed: C2.2, U1.13 (VDD)
unnamed: C1.2, U1.8 (VLOGIC)

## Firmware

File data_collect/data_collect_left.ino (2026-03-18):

#include <Arduino.h>
#include <Wire.h>
#include <Adafruit_MPU6050.h>
#include <Adafruit_Sensor.h>

#define thumbPin  0
#define indexPin  1
#define middlePin 2
#define ringPin   3
#define pinkyPin  4
#define i2cSda    6
#define i2cScl    7

const int openVals[5]   = {400, 400, 400, 400, 400};
const int closedVals[5] = {900, 900, 900, 900, 900};

Adafruit_MPU6050 mpu;

const int count = 30;
const int pace  = 50;

float getFlex(int pin, int slot) {
  return constrain(
    (float)(analogRead(pin) - openVals[slot]) / (float)(closedVals[slot] - openVals[slot]),
    0.0f, 1.0f
  );
}

void setup() {
  Serial.begin(115200);
  analogReadResolution(12);
  analogSetAttenuation(ADC_11db);
  Wire.begin(i2cSda, i2cScl);
  mpu.begin();
  mpu.setAccelerometerRange(MPU6050_RANGE_2_G);
  mpu.setGyroRange(MPU6050_RANGE_250_DEG);
  mpu.setFilterBandwidth(MPU6050_BAND_21_HZ);
  Serial.println("label,thumb,index,middle,ring,pinky,ax,ay,az,gx,gy,gz,timestamp");
}

void loop() {
  if (!Serial.available()) return;
  String label = Serial.readStringUntil('\n');
  label.trim();
  if (!label.length()) return;

  delay(500);
  for (int s = 0; s < count; s++) {
    sensors_event_t a, g, temp;
    mpu.getEvent(&a, &g, &temp);
    Serial.printf("%s,%.3f,%.3f,%.3f,%.3f,%.3f,%.3f,%.3f,%.3f,%.3f,%.3f,%.3f,%lu\n",
      label.c_str(),
      getFlex(thumbPin,0), getFlex(indexPin,1), getFlex(middlePin,2),
      getFlex(ringPin,3),  getFlex(pinkyPin,4),
      a.acceleration.x/9.81f, a.acceleration.y/9.81f, a.acceleration.z/9.81f,
      g.gyro.x, g.gyro.y, g.gyro.z,
      millis());
    delay(pace);
  }
}

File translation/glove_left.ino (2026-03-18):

#include <Arduino.h>
#include <BLEDevice.h>
#include <BLEServer.h>
#include <BLEUtils.h>
#include <BLE2902.h>
#include <Wire.h>
#include <Adafruit_MPU6050.h>
#include <Adafruit_Sensor.h>
#include <ArduinoJson.h>

#define thumbPin  0
#define indexPin  1
#define middlePin 2
#define ringPin   3
#define pinkyPin  4
#define i2cSda    6
#define i2cScl    7

#define serviceId  "4fafc201-1fb5-459e-8fcc-c5c9c331914b"
#define charId     "beb5483e-36e1-4688-b7f5-ea07361b26a8"
#define gloveName  "SIGNO-L"

const int openVals[5]   = {400, 400, 400, 400, 400};
const int closedVals[5] = {900, 900, 900, 900, 900};

BLEServer*         server = nullptr;
BLECharacteristic* characteristic = nullptr;
bool isConnected  = false;
bool wasConnected = false;

Adafruit_MPU6050 mpu;

#define smooth 4
int buf[5][smooth];
int idx = 0;

class BleCallbacks : public BLEServerCallbacks {
  void onConnect(BLEServer*)    override { isConnected = true; }
  void onDisconnect(BLEServer*) override { isConnected = false; }
};

float getFlex(int pin, int slot) {
  buf[slot][idx % smooth] = analogRead(pin);
  long sum = 0;
  for (int i = 0; i < smooth; i++) sum += buf[slot][i];
  float v = (float)(sum / smooth - openVals[slot]) / (float)(closedVals[slot] - openVals[slot]);
  return constrain(v, 0.0f, 1.0f);
}

void setup() {
  analogReadResolution(12);
  analogSetAttenuation(ADC_11db);
  memset(buf, 0, sizeof(buf));
  Wire.begin(i2cSda, i2cScl);
  mpu.begin();
  mpu.setAccelerometerRange(MPU6050_RANGE_2_G);
  mpu.setGyroRange(MPU6050_RANGE_250_DEG);
  mpu.setFilterBandwidth(MPU6050_BAND_21_HZ);

  BLEDevice::init(gloveName);
  server = BLEDevice::createServer();
  server->setCallbacks(new BleCallbacks());
  BLEService* svc = server->createService(serviceId);
  characteristic = svc->createCharacteristic(charId,
    BLECharacteristic::PROPERTY_READ | BLECharacteristic::PROPERTY_NOTIFY);
  characteristic->addDescriptor(new BLE2902());
  svc->start();
  BLEAdvertising* adv = BLEDevice::getAdvertising();
  adv->addServiceUUID(serviceId);
  adv->setScanResponse(true);
  adv->setMinPreferred(0x06);
  BLEDevice::startAdvertising();
}

unsigned long lastTime = 0;
const int pace = 50;

void loop() {
  if (!isConnected && wasConnected) { delay(500); server->startAdvertising(); wasConnected = false; }
  if (isConnected && !wasConnected)  wasConnected = true;

  if (isConnected && millis() - lastTime >= pace) {
    lastTime = millis();
    idx++;

    float flex[5] = {
      getFlex(thumbPin,0), getFlex(indexPin,1), getFlex(middlePin,2),
      getFlex(ringPin,3),  getFlex(pinkyPin,4)
    };
    sensors_event_t a, g, temp;
    mpu.getEvent(&a, &g, &temp);

    StaticJsonDocument<200> doc;
    doc["h"] = "L";
    JsonArray f = doc.createNestedArray("f");
    for (int i = 0; i < 5; i++) f.add(round(flex[i] * 1000) / 1000.0);
    JsonArray aArr = doc.createNestedArray("a");
    aArr.add(round(a.acceleration.x / 9.81f * 1000) / 1000.0);
    aArr.add(round(a.acceleration.y / 9.81f * 1000) / 1000.0);
    aArr.add(round(a.acceleration.z / 9.81f * 1000) / 1000.0);
    JsonArray gArr = doc.createNestedArray("g");
    gArr.add(round(g.gyro.x * 1000) / 1000.0);
    gArr.add(round(g.gyro.y * 1000) / 1000.0);
    gArr.add(round(g.gyro.z * 1000) / 1000.0);
    doc["t"] = millis();

    char out[200];
    serializeJson(doc, out);
    characteristic->setValue(out);
    characteristic->notify();
  }
}
